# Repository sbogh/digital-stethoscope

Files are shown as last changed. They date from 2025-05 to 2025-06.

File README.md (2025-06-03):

# ScopeFace: Digital Stethoscope

## Table of Contents
- [Introduction](#introduction)
- [Features](#features)
- [Team](#team)
- [Class Assignments](#class-assignments)
- [UX Research](#ux-research)
- [System Design](#system-design)
  - [UI Prototypes](#ui-prototypes)
  - [System Diagrams](#system-diagrams)
  - [Architecture](#architecture)
- [Repo Structure](#repo-structure)
- [Software](#software)
  - [Frontend](#frontend)
  - [Backend](#backend)
  - [Running the App](#running-the-app)
- [Hardware](#hardware)
  - [Setup](#setup)
  - [Operation](#operation)
  - [Assembly](#assembly)
- [Known Limitations](#known-limitations)
- [Future Work](#future-work)

## Introduction
**ScopeFace** is a portable digital stethoscope system developed over 10 weeks as part of UC San Diego's CSE 237D Embedded Systems Project course (Spring 2025). Our goal was to prototype a clinician-focused tool that amplifies, records, and replays heart and lung sounds through a streamlined mobile interface.

Designed with input from nurses, PAs, and doctors, the app supports session-based `.wav` recording, waveform visualization, note-taking, and Firebase-backed data storage. The hardware component captures sound using a custom-built stethoscope device, while the SwiftUI app allows users to review and annotate sessions in real time.

Check out our [external web presence here](https://myrmanshelby.github.io/digital-stethoscope-landing-page/)  
(External web presence [repo linked here](https://github.com/myrmanshelby/digital-stethoscope-landing-page)).

## Features
- Session-based `.wav` recording and playback  
- Waveform visualization  
- Session renaming and note-taking  
- Firebase integration for storage and authentication

## Team
- [Siya Rajpal](https://www.linkedin.com/in/siya-rajpal/): fullstack engineer
- [Shelby Myrman](https://www.linkedin.com/in/shelby-myrman/): ux design/frontend engineer
- [Amrita Moturi](https://www.linkedin.com/in/amrita-moturi/): hardware engineer
- [Shayan Boghani](https://www.linkedin.com/in/shayan-b/): hardware engineer

## Class Assignments
As part of UCSD's CSE 237D course, we created the following project artifacts:
- [Project Proposal](https://github.com/sbogh/digital-stethoscope/blob/main/admin/class-assignments/CSE_237D_Milestone_Report.pdf): A document detailing our project goals, MVP, and timeline
- [Milestone Report](https://github.com/sbogh/digital-stethoscope/blob/main/admin/class-assignments/CSE_237D_Milestone_Report.pdf): A document created halfway through the quarter to update our MVP and timeline
- [Project Update](https://github.com/sbogh/digital-stethoscope/blob/main/admin/class-assignments/ScopeFace%20Project%20Update-2.pdf): Our midquarter presentation updating the class on our progress

## UX Research
Before developing, we conducted user research interviews to gauge user needs. We then looked at app design inspiration and mapped in-app customer journeys. See our UX artifacts below:
- [User Interviews](https://github.com/sbogh/digital-stethoscope/blob/main/admin/user-research/user-research-summary.md)
- [Design Inpsiration](https://github.com/sbogh/digital-stethoscope/blob/main/admin/initial-diagrams/design-inspiration.pdf)
- [Initial User Journey Map](https://github.com/sbogh/digital-stethoscope/blob/main/admin/initial-diagrams/initial-user-journey.pdf)

## System Design

### UI Prototypes
We completed high-fidelity prototypes for both our MVP and ideal full system. 

#### MVP Prototypes
- [Login Flow](https://www.figma.com/design/D0sZ9Dy5eKCmVsZL9oDZRN/Digital-Stethoscope?node-id=1-34&t=OJdkmq2NDCs8I1Uz-1)
- [New Recording Page](https://www.figma.com/design/D0sZ9Dy5eKCmVsZL9oDZRN/Digital-Stethoscope?node-id=60-2107&t=OJdkmq2NDCs8I1Uz-1)

#### Reach System Prototypes
- [Learn More Flow](https://www.figma.com/design/D0sZ9Dy5eKCmVsZL9oDZRN/Digital-Stethoscope?node-id=38-15&t=OJdkmq2NDCs8I1Uz-1)
- [Home Page](https://www.figma.com/design/D0sZ9Dy5eKCmVsZL9oDZRN/Digital-Stethoscope?node-id=47-155&t=OJdkmq2NDCs8I1Uz-1)
- [FAQs Page](https://www.figma.com/design/D0sZ9Dy5eKCmVsZL9oDZRN/Digital-Stethoscope?node-id=60-2147&t=OJdkmq2NDCs8I1Uz-1)
- [History Flow](https://www.figma.com/design/D0sZ9Dy5eKCmVsZL9oDZRN/Digital-Stethoscope?node-id=60-2146&t=OJdkmq2NDCs8I1Uz-1)
- [Patient Flow](https://www.figma.com/design/D0sZ9Dy5eKCmVsZL9oDZRN/Digital-Stethoscope?node-id=78-3089&t=OJdkmq2NDCs8I1Uz-1)
- [Account Page](https://www.figma.com/design/D0sZ9Dy5eKCmVsZL9oDZRN/Digital-Stethoscope?node-id=52-3486&t=OJdkmq2NDCs8I1Uz-1)

### System Diagrams
We created 2 sets of system diagrams: our MVP system and our ideal full product system.
- **MVP System**: See our [MVP System Diagram here](https://github.com/sbogh/digital-stethoscope/blob/main/admin/mvp-product-diagrams/mvp-system-diagram.pdf) and our [MVP Database Schema Diagram here](https://github.com/sbogh/digital-stethoscope/blob/main/admin/mvp-product-diagrams/mvp-database-schema.pdf)
- **Full System**: See our [Full System Diagram here](https://github.com/sbogh/digital-stethoscope/blob/main/admin/full-product-diagrams/reach-system-diagram.pdf) and our [Full Database Schema Diagram here](https://github.com/sbogh/digital-stethoscope/blob/main/admin/full-product-diagrams/reach-database-schema.pdf)

For clearer views of our system diagrams, visit our [Miro board here](https://miro.com/app/board/uXjVI8VBn7o=/?share_link_id=259432345089).

### Architecture
- **Frontend**: SwiftUI-based iOS app tailored for clinician workflow (see [frontend ADR here](https://github.com/sbogh/digital-stethoscope/blob/main/admin/ADRs/042125-Swift.md))
- **Backend**: Python FastAPI service to support future device integrations and analytics (see [backend ADR here](https://github.com/sbogh/digital-stethoscope/blob/main/admin/ADRs/042125-Python-FastAPI.md))
- **Database**: Firebase Firestore and Authentication for secure session tracking (see [database ADR here](https://github.com/sbogh/digital-stethoscope/blob/main/admin/ADRs/042125-Firebase.md)) 
- **Hardware**: Custom stethoscope device with onboard mic and embedded microcontroller (see [all HW ADRs](https://github.com/sbogh/digital-stethoscope/tree/main/admin/ADRs))

## Repo Structure

```text
digital-stethoscope/
│
├── .github/                        # GitHub configuration files
│   └── workflows/                  # CI/CD pipeline setup (e.g., test and deploy scripts)
│
├── admin/                          # Documentation, planning assets, and research
│   ├── ADRs/                       # Architectural Decision Records
│   ├── class-assignments/         # Assignments submitted as part of CSE 237D
│   ├── full-product-diagrams/     # Diagrams for long-term vision of the system
│   ├── initial-diagrams/          # Early conceptual or low-fidelity diagrams
│   ├── mvp-product-diagrams/      # Diagrams focused on MVP system architecture
│   └── user-research/             # Notes and transcripts from stakeholder interviews
│
├── backend/                        # FastAPI backend services (e.g., API endpoints, auth)
│   ├── main.py                     # Entry point for the FastAPI app
│   └── ...                         # Additional modules, routes, and utilities
│
├── hardware/                       # Embedded systems and electronics
│   ├── modules/                    # Modular firmware for sensors, audio processing, etc.
│   ├── design/                     # Hardware design related information
│   │   ├── printing-files/         # CAD design files
│   └── ...                         # Circuit diagram, BOM, README for assembly instructions
│
├── digital-stethoscope/           # SwiftUI iOS app (Xcode project root)
│   └── digital-stethoscopeUITests # SwiftUI testing
│   ├── digital-stethoscope/       # Main app source folder
│   │   ├── Config/                # Environment settings, constants, Firebase setup
│   │   ├── Controllers/           # ViewModels and state management logic
│   │   ├── Extensions/            # Swift extensions for common utilities
│   │   ├── Models/                # Data structures for recordings, sessions, user state
│   │   └── Views/                 # SwiftUI interface components
│   │       ├── LearnMoreFlow/     # "Learn More" educational flow
│   │       ├── LoginFlow/         # Sign-in and account setup screens
│   │       └── RecordingsPage/    # Session list, audio playback, and note-taking
│   └── ...                        # Additional files for assets, userdata etc.
│
└── README.md                       # Project overview and documentation
```

## Software

### Frontend
1. Make sure you have Xcode downloaded on your computer.
2. The app is nested in folders of the same name. When you clone the respository, be sure to open digital-stethoscope/digital-stethoscope
3. Firebase SDK: You must install the Firebase SDK on your own machine.
    1. Navigate to the Project icon and right click (the first digital-stethoscope)
    2. Click on "Add Package Dependencies"
    3. In the search bar that pops up, paste this link: https://github.com/firebase/firebase-ios-sdk
    4. Click "Add Package"
    5. Then look through the list, adding Firebase Auth, Firebase Core, and Firebase FireStore to the target, which is just digital-stethoscope
4. Info.plist: Click on the projet icon one more time
    1. Navigate to the target (the icon labeled digital-stethoscope)
    2. Go to build settings, at the top, and click "all"
    3. Then search for "Generate Info.plist File". It should be under "Packaging". Make sure it is turned to No.
    4. Below that, there will be a field Info.plist File. Ensure the path to the Info file in the cell. 
5. Then you should be good to go!

### Backend
1. Make sure you have Python 3.10+ installed.
2. Make sure to have FastAPI installed
3. Take a look at main.py to get an idea of how everything works.
4. use ```uvicorn main:app --reload``` to run the server

### Testing

We used separate testing frameworks for the backend and frontend to ensure reliability across the system.

#### Backend (FastAPI + pytest)

All backend logic is tested using `pytest`.

To run backend tests:
    ```bash
    cd backend
    pytest

Make sure your virtual environment is activated and all dependencies from requirements.txt are installed.

**Test coverage includes:**
- Endpoint behavior
- Data validation
- Utility functions

#### Frontend (SwiftUI + XCTest)
Frontend tests were written using XCTest in Xcode.

To run frontend tests:
1. Open the Xcode project at digital-stethoscope/digital-stethoscope
2. In the Xcode menu, go to Product > Test

**Test coverage includes:**
- UI behavior of major views
- State updates and view model logic

All tests are located in the Tests group within the Xcode project navigator.

### Running the App
To run ScopeFace locally, start by launching the backend server and then run the iOS app through Xcode.
1. Install dependencies from the `requirements.txt` file:
   ```bash
   cd backend
   pip install -r requirements.txt 
2. Run the server
    ```bash
    uvicorn main:app --reload
3. Open the XCode project at digital-stethoscope/digital-stethoscope
4. Connect your iOS simulator or device and click run in Xcode.

## Hardware

### Setup
1. Using the Arduino IDE, plug in your XIAO ESP32-S3
2. Go to Tools -> PSRAM and enable "OPI PSRAM"
3. Add WiFi SSID and Password Information where specified in instruction comments
4. Add Firebase API Key and double check bucket and user authentication information
5. Compile and upload to microcontroller

### Operation
1. Wait for upload to complete and check for initialization success (serial monitor will display WiFi connected, Firebase connected)
2. Press button to record 30 seconds of audio (LED will be red)
3. Wait for Firebase upload to complete (LED will be green)
4. Navigate to Firebase to playback audio

### Assembly
Please see the BOM [here](https://github.com/sbogh/digital-stethoscope/blob/main/hardware/design/ScopeFace%20BOM.xlsx) for information on the parts you need. See the README [here](https://github.com/sbogh/digital-stethoscope/tree/main/hardware/design#readme) for instructions on creating and assembling the device.

## Known Limitations

- Currently runs only on the iOS simulator (no physical deployment)
- No patient or date search functionality
- No HIPAA compliance implemented
- ML diagnostics and patient profiles are not yet developed

## Future Work

While our MVP successfully supports audio recording and playback through a mobile interface, we do not plan to continue developing this product beyond the scope of our course. However, if we were to bring the app to market, the following areas represent logical extensions based on our prototypes and system design:

### HIPAA Compliance
To prepare the system for real-world clinical use, we would need to implement full HIPAA compliance. This would include encrypted data storage, authenticated access, and audit logging to ensure secure handling of sensitive health information.

### Patient Assignment and Record Management
A full version of the app could support assigning heartbeat and lung recordings to individual patients. This might include:
- Patient profiles
- Recording tagging and linking

See our [Patient Flow Prototype](https://www.figma.com/design/D0sZ9Dy5eKCmVsZL9oDZRN/Digital-Stethoscope?node-id=78-3089&t=OJdkmq2NDCs8I1Uz-1) and [Full System Diagram](https://github.com/sbogh/digital-stethoscope/blob/main/admin/full-product-diagrams/reach-system-diagram.pdf) for intended design.

### History and Session Review
We envisioned adding a history view to allow clinicians to filter by date, patient, or condition to access recordings.

See our [History Flow Prototype](https://www.figma.com/design/D0sZ9Dy5eKCmVsZL9oDZRN/Digital-Stethoscope?node-id=60-2146&t=OJdkmq2NDCs8I1Uz-1).

### Improved Home and Recordings Pages
In a production-ready version, the home and recordings pages could be enhanced to include streamlined navigation across patients and sessions

See our [Home Page Prototype](https://www.figma.com/design/D0sZ9Dy5eKCmVsZL9oDZRN/Digital-Stethoscope?node-id=47-155&t=OJdkmq2NDCs8I1Uz-1) compared to our [MVP Recordings Page](https://www.figma.com/design/D0sZ9Dy5eKCmVsZL9oDZRN/Digital-Stethoscope?node-id=60-2107&t=OJdkmq2NDCs8I1Uz-1).

### Machine Learning for Diagnostics
If continued, we could explore machine learning models for analyzing heart and lung sounds. Features might include:
- On-device or server-side analysis
- Detection of irregular rhythms, murmurs, or wheezing
- Clinician-facing summaries of algorithmic findings

This concept would be positioned as decision support rather than automated diagnosis.

### Deployment and TestFlight
Currently, the app can only be run on a simulator due to the cost of an Apple Developer account. In a future rollout, we would:
- Register for an Apple Developer account
- Use TestFlight to distribute builds to physical devices
- Consider submitting to the App Store for clinical pilots

---

These potential extensions align with the user needs captured in our [User Interviews](https://github.com/sbogh/digital-stethoscope/blob/main/admin/user-research/user-research-summary.md) and the architecture outlined in our [Miro board](https://miro.com/app/board/uXjVI8VBn7o=/?share_link_id=259432345089).

## Contributing
This project is no longer actively maintained, but if you'd like to fork or reuse components, feel free to open issues or pull requests.

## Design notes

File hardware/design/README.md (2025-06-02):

# Assembly Instructions
This document will provide a guide to assembling the ScopeFace Digital Stethoscope. To begin, please review the BOM and ensure you have all of these parts. You will also need 22 AWG Wire, a Soldering Iron, Electrical Tape, PET-G, and a 3D Printer.

First, we will do some preparation work:
1. Solder pieces of 22 AWG wire (longer than you think you'll need) to the following pins of the microphone evaluation board: WS, SCK, Data, GND, VDD. Try to use different colors for easy distinguishing.
2. Solder the Male to Female Battery connector to the XIAO ESP32-S3. Ensure to solder the correct leads. See [here](https://wiki.seeedstudio.com/xiao_esp32s3_getting_started/#battery-usage) for specific instructions.
3. Desolder the button wires and solder them so they go upwards rather than straight outwards. This will help with space management.
4. Solder resistors to the LED leads (only Red and Green). Clip off the Blue lead.

Now we can put together the parts:
1. Print all of the parts found in /printing-files on your 3D Printer in PET-G
2. Take the heated threaded inserts and place them inside the holes on the Diaphragm and Mic Mount. They should slide in all the way except the top section which is not tapered. Using a soldering iron, set these inserts into the part so they are flush with the top surface of the standoffs.
3. Slide the battery into the Battery Mount. Ensure that the wire lead faces the inside of the body and slide it through the small opening to have the wires stick out as the battery sits inside the part.
4. Slide the mic evaluation board into the slot on the Diaphragm and Mic Mount. It should press fit (it is VERY tight so be absolutely sure the pick up hole on the mic board lines up with the hole on the part before pressing it down).
5. Stack the ESP32 Mount and the Battery Mount on top of the Diaphragm and Mic Mount. Using the M2-0.4 x 12 mm bolts secure these parts together using diagonal holes (2 of the four slots). IMPORTANT: route the wires from the battery on the inside of the standoffs so that it sits tightly between the Battery Mount and the standoffs.
6. Place the XIAO ESP32-S3 into the ESP32 Mount. It should slide in and be held in place. Solder the mic evaluation board WS, SCK, and Data cables (see the wiring diagram for specific pins).
7. Take Casing Cover and slide the push button into its slot.
8. Solder the 3.3V power to the microphone board cable (VDD) and the push button NEGATIVE lead.
9. Solder the push button POSITIVE lead to its GPIO pin (see [wiring diagram](https://github.com/sbogh/digital-stethoscope/blob/main/hardware/design/Wiring%20Diagram.png)).
10. Slide the LED into its slot. Solder the red and green pins to their respective GPIO ports (see [wiring diagram](https://github.com/sbogh/digital-stethoscope/blob/main/hardware/design/Wiring%20Diagram.png)).
11. Solder GND to the microphone board (GND) and the LED common ground pin.
12. Attach the antenna to the XIAO ESP32-S3. ([link](https://wiki.seeedstudio.com/xiao_esp32s3_getting_started/#installation-of-antenna))
13. Line up the USB-C opening on the Casing Cover to the XIAO ESP32-S3 port (the button should be opposite to this face) and slide the cover on. It will be tight so be careful to ensure no pinched wires.
14. Use the M2-0.4 X 25 mm bolts to secure the Casing Cover to the heated threaded inserts.
15. Slide the stethoscope diaphragm cover onto the Diaphragm and Mic Mount. It will stretch onto the bottom lip.

Now you can enjoy your ScopeFace Stethoscope!

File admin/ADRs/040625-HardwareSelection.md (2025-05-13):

# Architecture Decision Record: Hardware selection

**Status**: Accepted  
**Date**: 2025-04-06  

---

## 1. Context

Our first stage for hardware selection was determining a good fit for the main component of our embedded system. There are options like the Raspberry Pi (single-board computer), Arduino boards (microcontroller), ESP32 (microcontroller), and others. The selected hardware needs to be capable of connecting components to record and process heart and lung sounds, transmit data wirelessly, and potentially run classification models.

## 2. Decision

Our project requirements lean towards the use of a microcontroller.

## 3. Rationale

A SBC is more complex than is needed for this project given the straightforward use case. Additionally, size constraints make it so that a microcontroller may be a better choice for the product form factor. Potential stretch goals, like onboard ML inference, can still be explored using higher-end microcontrollers like the ESP32-S3.

## 4. Consequences

### Positive outcomes

- Lower cost and power requirements
- Smaller physical footprint
- Easier integration with embedded peripherals like microphones
- Faster development for real-time, single-purpose firmware

### Negative outcomes
- Limited processing power may constrain future ML capabilities or advanced signal
processing

## 5. Alternatives Considered

- Raspberry Pi (e.g., Pico W): Rejected due to lack of Bluetooth on Pico W, higher cost and power usage on full-size Pi models, and overkill for the use case.

- STM32 family: Not chosen due to longer learning curve and less community documentation compared to ESP32.

- ESP32-WROOM-32 / ESP32-S3: These were selected as microcontroller options based on processing capability, wireless features, and documentation maturity.

## 6. References

Raspberry Pi Pico documentation [https://www.raspberrypi.com/documentation/microcontrollers/pico-series.html]

STM32 32-bit Arm Cortex MCUs
[https://www.st.com/en/microcontrollers-microprocessors/stm32-32-bit-arm-cortex-mcus/documentation.html]

ESP32-S3 datasheet and Espressif documentation [https://www.espressif.com/sites/default/files/documentation/esp32-s3_datasheet_en.pdf]

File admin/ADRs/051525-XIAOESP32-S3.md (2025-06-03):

# Architecture Decision Record: [Transition to Seeed Studio XIAO ESP32S3 Plus]

**Status**: [Accepted]  
**Date**: [2025-05-15]  

---

## 1. Context

 Our initial prototype used the standard ESP32-S3 development board. However, the size of the ESP32-S3 dev board created a major constraint for integrating the device into a small shell suitable for clinical or at-home use.

We also wanted to avoid the complexity and cost of designing a custom PCB, as our timeline prioritized rapid prototyping and iteration.
## 2. Decision

We have decided to transition from the standard ESP32-S3 development board to the Seeed Studio XIAO ESP32S3 Plus.

## 3. Rationale

The Seeed Studio XIAO ESP32S3 Plus was selected for the following reasons:

Smaller footprint: The XIAO board’s compact size (21 × 17.5 mm) allows it to be directly integrated into our 3D-printed stethoscope housing without requiring a custom PCB.

Built-in features: The Plus variant includes integrated USB-C, battery charging, and flash/RAM (8MB PSRAM, 16MB flash), which are needed for onboard audio buffering and wireless transmission tasks.

Maintains ESP32-S3 architecture: This transition retains compatibility with our existing codebase, libraries, and development tools.

## 4. Consequences

### Positive outcomes:

Enables a complete prototype build within a standard stethoscope form factor.

Avoids custom PCB design during initial development.

Reduces cost and lead time for prototyping iterations.

Maintains ESP32 toolchain and firmware compatibility.

### Negative outcomes:

May require RF tuning or external antenna in final design if extended WiFi range is needed.

Tighter GPIO constraints and mechanical routing limitations may limit future peripheral expansions.

### Process Changes:

Firmware adapted to match the XIAO ESP32S3 Plus pinout.

CAD models for enclosure updated for new board dimensions and connectors.

Charging and power management tested using integrated USB-C and minimal LiPo battery setup.

## 5. Alternatives Considered

LilyGo T7 S3: Technical specs were sufficient, but was ruled out due to sourcing issues—high price, limited availability, and long shipping times.

## 6. References

Seeed Studio XIAO ESP32S3 Plus (16 MB Flash, 8 MB PSRAM):
https://www.seeedstudio.com/Seeed-Studio-XIAO-ESP32S3-Plus-p-6361.html

LilyGo T7 S3:
https://lilygo.cc/products/t7-s3

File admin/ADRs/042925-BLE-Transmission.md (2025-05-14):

# Architecture Decision Record: Bluetooth Audio Transmission

**Status**: Accepted  
**Date**: 2025-04-25  

---

## 1. Context

The team explored how to transmit audio data from the ESP32 microcontroller to an iPhone via Bluetooth and considered possible architecture designs to handle audio file storage and avoid data loss during transmission.
## 2. Decision

We investigated Bluetooth audio transmission using the ESP32 A2DP profile and a timer-based audio recording trigger (e.g., press button → record for X seconds). We also decided to integrate a microSD card interface for local storage of audio prior to transmission.
## 3. Rationale

The ESP32 supports A2DP (Advanced Audio Distribution Profile) for Bluetooth audio streaming, which seems to be standard. iOS places limitations on BLE connections (such as MTU, packet limitations, transmission intervals). 
For the timer-based recording, this simplifies our firmware logic so that we can press record, record for a fixed time, and auto stop. Local storage via microSD ensures recordings are not lost due to unstable wireless conditions.

## 4. Consequences

### Positive outcomes

- Reduced risk of data loss with local microSD buffering

### Negative outcomes
- Potential delays in file upload if relying on local storage

- Need to manage microSD read/write cycles and file system handling

- Increased firmware and hardware complexity for SD card integration and buffer management

### Changes to processes/systems
- Introduce SD card write/delete logic into embedded software

- Need to evaluate packet framing strategies for .wav file reconstruction (header + raw data)

## 5. Alternatives Considered

Potential pivots based on iOS BLE connection limitations:  Have ESP32 connect either directly to a cloud server gateway or use the app as an authentication gateway to make connection with cloud server and have data transmitted directly there rather than to the iPhone.

## 6. References
Guide for MicroSD Card Module using Arduino IDE
[https://randomnerdtutorials.com/esp32-microsd-card-arduino/]

Challenges in Bluetooth Low Energy (BLE) Integration with iOS Devices
[https://www.zco.com/blog/challenges-in-ble-integration-with-ios-devices/]

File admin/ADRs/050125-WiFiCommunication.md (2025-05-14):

# Architecture Decision Record: Pivot to WiFi Communication and microSD-Based File Storage with Firebase Integration

**Status**: Superseded
**Date**: 2025-05-01

---

## 1. Context

The team initially explored how to transmit audio data from the ESP32 microcontroller to an iPhone via Bluetooth. However, BLE limitations including connection instability, low MTU size, and complexity in handling large file transfers led to reevaluation.

## 2. Decision
Pivot from BLE to WiFi for uploading audio data from the ESP32. We also decided to use Firebase as the backend for file uploads and database management.

## 3. Rationale
- WiFi offers higher bandwidth and greater reliability than BLE for transmitting large audio files. It also avoids limitations of iOS BLE stack, including lack of native BLE file transfer interfaces.

- TA recommendation confirmed WiFi would be more practical within the project’s scope and timeline.
- Firebase is easy-to-integrate with ESP32 and the front-end team was familiar with the framework.

## 4. Consequences

### Positive outcomes
WiFi transmission
- More reliable data transmission via WiFi
  
-  Easier integration with mobile frontend through Firebase

Firebase:
- Provides secure file hosting and database access

- Frontend can easily pull data directly from Firebase without complex middleware

### Negative outcomes
N/A

## 5. Alternatives Considered

As mentioned, we pivoted away from BLE transmission of audio data.
## 6. Related Decisions
BLE Transmission ADR [https://github.com/sbogh/digital-stethoscope/blob/main/admin/ADRs/050925-BLE-Transmission.md]

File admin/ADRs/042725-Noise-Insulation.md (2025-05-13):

# Architecture Decision Record: Noise Insulation Strategy

**Status**: Accepted 
**Date**: 2025-04-27 

---

## 1. Context

During testing, it became clear that the microphone alone was too sensitive to ambient noise. To address this, the team researched acoustic insulation strategies to shield the microphone from external noise sources.
## 2. Decision

Based on our research, we will prototype a noise insulation solution using a construction-grade ear protection cup as a sound-dampening casing for the microphone. We will route microphone wiring through the ear cup and seal it to prevent sound leakage.

## 3. Rationale

The microphone is highly sensitive and picks up unwanted ambient sounds, which hinders the clarity of heartbeat/lung sounds. A construction ear protector offers a cost-effective and accessible solution for prototyping a noise-insulating material.

## 4. Consequences

### Positive outcomes
- Minimal-cost prototype with quick testability using off-the-shelf materials
### Negative outcomes
- Drilling ear cup and sealing introduces irreversible changes to prototype components

### Any changes to processes, systems, or dependencies
- Microphone wiring must be adapted to route through physical insulation

## 5. Alternatives Considered

Using commercial stethoscope housing: Considered overkill for early prototyping and lacks flexibility.
## 6. Related Decisions

N/A

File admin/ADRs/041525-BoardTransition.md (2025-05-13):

# Architecture Decision Record: Transition to ESP-WROOM-32 with Digital Microphone

**Status**: Accepted  
**Date**: 2025-04-15  

---

## 1. Context

The team conducted testing with both analog and digital microphones on selected MCU boards (ESP32-S3 and ESP-WROOM-32) to identify the best microphone for capturing heart/lung sounds and verify compatibility with the microcontroller platform.

## 2. Decision

Microphone testing occurred and based on outcome the digital microphone was chosen. The initial ESP32 S3 board failed to interface with the microphone so the ESP-WROOM-32 has been made the primary board.

## 3. Rationale

Mic Selection: 
- The analog microphone (MAX4466) suffered from heavy power supply noise and delivered poor sound quality, and failed to filter noise effectively.

- The digital microphone (INMP441) leveraged the I2S interface on ESP32 boards allowing seamless and quick setup.

- The use of a digital mic also eliminates the need for external ADCs, simplifying hardware design.

Board Selection:

- The ESP32-S3 failed to recognize any serial data over I2S from the INMP441 during testing.

- The ESP-WROOM-32 successfully captured audio from the digital microphone and was thus selected as the new primary board for development.

Additional considerations included:

- Aliasing and mssing low frequencies: These issues can be mitigated by selecting an appropriately high sampling rate.

- File size and audio compression: The raw audio data can be stored in WAV format (lossless) or transmitted as raw bytes and reconstructed server-side

- Bluetooth transmission limits: Live streaming of audio via BLE may not be feasible; however, delayed upload is acceptable our use case.

## 4. Consequences

### Positive outcomes

- Improved audio quality and reduced noise using INMP441
- More stable and compatible development environment using ESP-WROOM-32
- Simplified integration path via I2S (no need for ADC)

### Negative outcomes
- Not using the ESP32-S3 forfeits potential for onboard AI inference unless revisited

### Changes to processes/systems
- Transition away from analog signal processing to digital-only audio handling

- Firmware updates to focus exclusively on I2S and ESP-WROOM-32 compatibility

- Audio files will likely be recorded in WAV format

## 5. Alternatives Considered

N/A

## 6. Related Decisions
MCU Decision
[https://github.com/sbogh/digital-stethoscope/blob/main/admin/ADRs/040725-MCU-Decision.md]

Mic Selection
[https://github.com/sbogh/digital-stethoscope/blob/main/admin/ADRs/040825-MicSelection.md]

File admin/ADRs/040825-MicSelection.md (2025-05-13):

# Architecture Decision Record: Microphone selection

**Status**: Accepted  
**Date**: 2025-04-08 

---

## 1. Context

The team decided to test both analog and digital microphones with the devices to determine the best device to use to capture heart and lung sounds. The microphones with the correct frequency ranges are difficult to source so initial testing will be done with common microphones easily available and then when a decision is made (between digital and analog), the microphone will be swapped for the true device.

## 2. Decision

Our team decided to test both an analog microphone (MAX4466) and a digital microphone (INMP441).

## 3. Rationale

Frequency range: Both MAX4466 and INMP441 can support frequencies near the required 20–3000 Hz range.

Sampling rate: Both mics support a sampling rate 2x of highest frequency

Availability and cost: Both microphones are inexpensive and widely available, which is ideal for our initial prototype.

## 4. Consequences

### Positive outcomes

- INMP441 (digital): Uses I2S protocol, avoiding analog signal interference. I2S is natively supported on ESP32 and has reliable open-source examples and community support.

### Negative outcomes
- MAX4466 (analog) requires analog-to-digital conversion (ADC) and may introduce analog noise. Also, the ESP32-S3 does not have built-in ADC, requiring external components.

## 5. Alternatives Considered

N/A

## 6. References

Heart and lung frequencies [https://pmc.ncbi.nlm.nih.gov/articles/PMC2990233/#:~:text=The%20spectrum%20of%20heart%20sounds,like%20fine%20or%20coarse%20crackles.]

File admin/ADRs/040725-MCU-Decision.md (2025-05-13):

# Architecture Decision Record: MCU decision

**Status**: Accepted 
**Date**: 2025-04-07 

---

## 1. Context

The team decided on an MCU after considering other embedded device options due to the need for the system to be low-cost and being able to handle wireless connectivity and potentially ML inferencing.

## 2. Decision

Based on the stretch goal the ESP32 S3 was chosen, with the ESP-WROOM-32 chosen as a secondary fallback.

## 3. Rationale

Key considerations included budget constraints, time constraints (well documented board), and connectivity functionality (need for BLE/WiFi).
ESP32 S3 contains a strong processing unit capable of onboard inference for an AI model (a potential stretch goal for the team)

## 4. Consequences

### Positive outcomes
- The ESP32-S3 Dev Module has strong processing capabilities, allowing future support for onboard AI inference
- Leverages well-supported and cost-effective components
### Negative outcomes
- ESP32 S3 does not contain built-in ADC so audio out would likely require additional components
- ESP32-S3 is newer, so some libraries or integrations may be less mature than ESP-WROOM-32.

### Any changes to processes, systems, or dependencies
- Since ESP32 S3 does not contain an ADC, we may have to consider other mic interfaces like I2S

## 5. Alternatives Considered

Arduino Nano ESP32 user experience research shows that the interface is not aligned with traditional ESP32 use and will require additional research to understand some niche aspects of connecting peripheral devices
ESP-WROOM-32 is the best documented of all devices, but may not be able to handle the ML inferencing computational requirement.

## 6. Related Decisions

N/A

## 7. References

Esp32-wroom-32 docs [https://www.espressif.com/sites/default/files/documentation/esp32-wroom-32_datasheet_en.pdf]

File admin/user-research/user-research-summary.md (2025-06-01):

# User Research Summary

## April 2, 2025: Shelby's Discussion with Nurses

### Requested Use Cases from a Small Sample of Nurses and Physician Assistants

#### Cost
- Stethoscopes are expensive, often costing at least $100 out of pocket.
- Nurses prioritize performance and are willing to pay for quality.
- **Our solution**: Create a significantly more affordable alternative.

#### Difficulty Hearing
- Nurses report that stethoscope sounds are often too quiet.
- One nurse was unable to hear wheezing that her trainer could, even after repeated attempts.
- **Our solution**: Integrate sound amplification.

#### Confirming Sounds with Doctors
- A nurse identified a murmur that was not heard by a physician during follow-up, leading to uncertainty.
- Having a recording to replay for confirmation would be helpful.
- **Our solution**: Enable sound recording and playback.

#### Difficulty Counting
- Nurses struggle with counting beats per minute (BPM) and respirations while listening for anomalies.
- **Our solution**: Provide automatic BPM and respiration rate counting.

#### Portability and Usability
- Nurses often misplace stethoscopes.
- Pediatric nurses report that traditional stethoscopes can scare children.
- **Our solution**: Consider a compact, wearable, or pin-based form factor with a friendly design.

#### Live Listening
- Some assessments are time-sensitive and require immediate feedback.
- **Our solution**: Support live listening via speakers or Bluetooth-connected headphones.

---

## Other Considerations

### Pediatric Use
- Traditional stethoscopes have a baby-specific diaphragm.
- Using the adult side on a baby results in excessive noise and poor sound isolation.
- **Note**: Our design may need a smaller sensor or a separate pediatric version.

### Machine Learning Diagnostics
- Nurses support ML-aided diagnostics, but prioritize reliable amplification and recording.
- Users want access to recordings even if automated diagnosis is included.
- **Our solution**: Focus on recording, with ML as an optional aid.

### Lungs
- Stethoscopes are also used for lung auscultation.
- Lung and heart sounds are distinct; users may need to indicate which organ is being monitored.
- **Our solution**: Offer a simple toggle between heart and lung modes.

---

## April 4, 2025: Shayan’s Discussion with a Doctor

### Clinical Use Cases During Exams

#### Heart Rate
- Categories: bradycardia, normal (60–100 bpm), tachycardia

#### Rhythm
- Regular or irregular
  - Irregularly irregular (e.g. atrial fibrillation)
  - Episodic irregular
  - Premature beat

#### Heart Sounds
- S1: Closure of mitral and tricuspid valves
- S2: Closure of aortic and pulmonary valves

##### Important Sound Features
- Sound intensity: muffled, too loud, normal
- Split sounds: generally not prominent in adults
  - S1: mitral before tricuspid
  - S2: aortic before pulmonary
- Murmurs: may indicate normal or pathological flow
  - Example: anemia can cause high flow murmurs

##### Murmur Classification
- Phase: systolic (S1–S2) or diastolic
- Timing: early, late, throughout
- Special case: machinery murmur (present in both phases)

#### Note
- Many doctors now rely on ECGs instead of stethoscopes.

---

## April 4, 2025: Amrita’s Meeting with Nicolay (Sensor Specialist)

### Technical Feedback and Suggestions

- The stethoscope’s listening component is complex enough to justify a full project focus.
- Consider creating a disposable patch version with external electronics.
- Companies in this space include Eko and Korean pet care companies using Bluetooth-enabled stethoscopes.

### Hardware Considerations

- Evaluate whether the **NDP120** chip can handle onboard inferencing.
- Explore **PDM** output format for sensor-to-dev board interfacing.
- Use an **audio codec chip** to translate raw sensor data into a usable format.

### Sensor Recommendations

- Consider analog sensors for better compatibility with audio processing.
- Prioritize small form factor and low noise for clean signal capture.
- V2S sensor operates at 10 kHz, but heart sounds are below 500 Hz.
  - Excessive bandwidth introduces noise; filtering is necessary.
  - Prefer sensors with native bandwidth under 1 kHz.

### Additional Notes

- Explore accelerometers and vibration sensors as alternatives.
- Arduino Nano 33 supports PDM input and could be a good prototyping option.

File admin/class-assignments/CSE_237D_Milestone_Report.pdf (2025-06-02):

# CSE 237D: Digital Stethoscope Milestone Report

### Amrita Moturi, Shayan Boghani, Shelby Myrman, Siya Rajpal

UC San Diego Computer Science & Engineering Dept.

## MVP Progress

### Proposed MVP

In our Project Specification Report, we laid out our initial vision for our original MVP below.
The goal of our Minimum Viable Product (MVP) is to develop a fully functional and portable digital stethoscope that captures, amplifies, records, and visualizes heart and lung sounds. This MVP serves as a proof-of-concept, providing the foundational system architecture for our broader vision while allowing us to gather early user feedback and iterate over time. Our emphasis is on incremental improvement: each core function is selected for high feasibility and clear alignment with the project’s long-term clinical goals which can be decoupled and tested as we make progress.

Core MVP Components

1. Acoustic Signal Acquisition: The MVP will use a digital microphone with sensitivity in the appropriate frequency bands for heart and lung sounds. The system will be integrated into a robust enclosure modeled after existing stethoscope chest pieces to facilitate familiarity and ergonomics.
2. Recording and Playback: The MVP must reliably capture sound data for local storage and enable playback through either a speaker or through the front end software interface. Data will be stored securely

1

and labeled with timestamps, creating a foundation for potential clinical documentation or further diagnostic analysis.

3. Portable and Durable Hardware Design: The stethoscope will be encased in a 3D-printed shell that is both lightweight and resilient. It will house the microcontroller, power supply (battery), and microphone. The prototype will prioritize modularity to support future iterations, such as integration of custom PCBs or embedded ML components.
4. Visualization via Companion Interface: The MVP will include a simple user interface (UI) that visualizes the sound waveform and increases the sound captured by the device. This UI will be implemented either as a mobile app based on preliminary user research and will focus on clarity and usability. The visualization and audio allows real-time signal monitoring, enabling both users and potential clinical testers to assess stethoscope performance.

The MVP is intentionally narrow in scope but complete in functionality. Each feature is selected to highlight a critical part of the user experience and overall system integrity. The emphasis is not on completeness or polish but on creating an end-to-end experience that can be tested, validated, and iterated upon. By grounding the MVP in core biomedical functionality (amplification, recording, and visualization), we create a minimum usable product that is meaningful to stakeholders and can evolve based on feedback.
The MVP enables us to evaluate core assumptions about hardware compatibility, UI requirements, and clinical relevance before committing to more complex features such as headphone integration, HIPAA compliance, edge ML deployment, or custom PCB creation. It also provides an anchor for testing usability, sound quality, and data handling practices early in the development lifecycle. Ultimately, our MVP will demonstrate that a portable, secure, and intelligible digital stethoscope can serve as a launchpad for more advanced diagnostic tools and integration with health information systems.

### MVP Progress Evaluation

The above four key components of our MVP can be individually evaluated to determine the team’s progress.

2

1. Acoustic Signal Acquisition: The current device now uses a digital I2S microphone that has the proper frequency band to acquire heart and lung sounds. This microphone took some time to source, and as such testing was done with a more commonly available microphone. However, the microphone was swapped out and has been tested in the audio pipeline that was built out previously.
2. Recording and Playback: The audio pipeline has been rigorously tested to ensure robust quality throughout. The device is able to record and transmit information consistently and effectively for playback from our secure database. Each recording has metadata including: Device ID, Recording ID Number, and Reception Timestamp. These three identifiers allow for easy identification of each new recording.
3. Portable and Durable Hardware Design: This aspect of the device is currently a work in progress. The remainder of the quarter will be dedicated to creating this housing and testing it. This task will entail: designing the casing which allows the microphone to pick up key frequencies, ensuring this casing is robust (drop and water resistance), and finally integrating feedback into the casing design based on further user research.
4. Visualization via Companion Interface: This aspect of the product is currently a work in progress. We have developed the login, authentication, and most of the front-end of the new recording page. During week 7-8, we will pull device data from Firebase for the new recordings page and visualize the waveforms in the app. Additionally, while the data will be retrieved quickly, we will not monitor the signal in real-time, and there may be a lag due to our logistic and privacy-based decision to not upload from the device directly to a user’s phone. We have accounted for this in our UX design to ensure the user experience still feels seamless.

### Milestone and Deliverable Progress

Below, we lay out the milestones and deliverables proposed in our initial report and display the progress made as of this report.

3

Hardware

- Deliverable 1 (Week 3): Hardware Schematic Diagram (Amrita)
Proof: Document with all major hardware components mapped out Milestones:

– Determine and list major components needed based on final product requirements

– Determine connections and additional interfacing components

Progress: Here (https://docs.google.com/spreadsheets/d/1qTJ2odaX2M_xSuLlmmqz6MXSB-b1hMWjHKfpnbmQvbA/edit?usp=sharing) is the BOM regarding the critical components related to the hardware. This has been updated since Week 3 to reflect iterations in the hardware. Here (https://docs.google.com/drawings/d/1nCev1_cij9lSaxVhKZNDl6bqoeuCaXK7Ml2xmFv6oDM/edit?usp=sharing) is the Hardware Schematic Diagram which shows how the different components must be mapped/connected.

- Deliverable 2 (Week 3): Hardware Selection Decision (Shayan) Proof: Bill of materials based on hardware schematic diagram Milestones:

– Research and downselect microcontrollers

– Test microphones for heart and lung sound frequencies

– Decide on filtering approach (analog and/or digital) to isolate target frequency bands for heart (typically 20–150 Hz) and lung (100–1000 Hz) sounds

Progress: As referenced above, the BOM also served as the list of major components needed. Here (https://docs.google.com/spreadsheets/d/1qTJ2odaX2M_xSuLlmmqz6MXSB-b1hMWjHKfpnbmQvbA/edit?usp=sharing) is the BOM which includes the chosen microcontroller and microphone with the proper frequency range. This document (https://docs.google.com/document/d/19m3-ZZDV7gM7EtZsWnEW9_dwk2fAkhaoKPsgd79wpz4/edit?usp=sharing) contains details in how the hardware was chosen.

– Hardware Selection ADR: (https://github.com/sbogh/digital-stethoscope/blob/main/admin/ADRs/040625-HardwareSelection.md) Explains our decision to use a microcontroller for our system

– MCU ADR: (https://github.com/sbogh/digital-stethoscope/blob/main/admin/ADRs/040725-MCU-Decision.md) justifies our use of the ESP32 S3

– Microphone Selection ADR: (https://github.com/sbogh/digital-stethoscope/blob/main/admin/ADRs/040825-MicSelection.md) provides context for use of MAX4466 (analog) and INMP441 (digital) mics

– Board Transition ADR: (https://github.com/sbogh/digital-stethoscope/blob/main/admin/ADRs/041525-BoardTransition.md) describes our initial transition to ESP-WROOM-32 board

4

- Deliverable 3 (Week 5): Initial Product Prototype (Shayan) Proof: Prototype with fully integrated hardware components Milestones:

– Order and assemble hardware

– Wire components, create documentation and diagram

Progress: The initial hardware prototype can be seen in the demo video here. (https://drive.google.com/file/d/16t6yuFCVIlv_w8SWK52N-YrlvbcqlBcp/view?usp=sharing) A newer, more streamlined version can be seen here. (https://drive.google.com/file/d/12NFOvNi5C9KDR8bGgvmpbmkIhpaNUu-6/view?usp=sharing)

- Deliverable 4 (Week 5): Initial Prototype Code (Amrita) Proof: Run and test hardware code, graphs showing frequency response before and after filtering, video demonstration
Milestones:

– Microphone data acquisition and processing

– Recording functionality

– Implement digital filtering to isolate relevant sound frequencies

– Transmit data from microcontroller to device

Progress: The initial prototype code can be seen functioning in the demo video here. (https://drive.google.com/file/d/16t6yuFCVIlv_w8SWK52N-YrlvbcqlBcp/view?usp=sharing) The source code can be found in the GitHub repository here. (https://github.com/sbogh/digital-stethoscope/blob/main/hardware/hardware.ino)

Software

- Deliverable 1 (Week 2): Tech Stack Decision (Shelby) Proof: Tech stack list and rationale
Milestones:

– Compare options and finalize stack

– Write setup guide

Progress: We have finalized our software technology stack, completed the setup guide, and documented our decisions in a series of ADRs.

– Setup Guide: (https://github.com/sbogh/digital-stethoscope/blob/main/README.md) Explains how to run our demo code after downloading the repository.

5

– Firebase ADR: (https://github.com/sbogh/digital-stethoscope/blob/main/admin/ADRs/042125-Firebase.md) justifies our use of Firebase Authentication and Firestore for backend data storage and user management

– SwiftUI ADR: (https://github.com/sbogh/digital-stethoscope/blob/main/admin/ADRs/042125-Swift.md) describes our decision to use Swift and SwiftUI based on user preference for native iOS apps

– Python/FastAPI ADR: (https://github.com/sbogh/digital-stethoscope/blob/main/admin/ADRs/042125-Python-FastAPI.md) outlines why we chose Python with FastAPI for our backend services

- Deliverable 2 (Week 2): GitHub Setup (Siya)
Proof: Screenshot of repo and CI/CD pipeline Milestones:

– Initialize repo

– Add CI/CD for linting and testing

Progress: We have created our repository and organized it. A screenshot of it can be seen Here. (https://drive.google.com/file/d/1JFufRA8rSI2mRyEmdqVacoP95BO5NVBz/view?usp=sharing) We chose to organize the repository by hardware code, backend software code, and our Xcode project, digital stethoscope. We have also included an admin folder in which you can find our system diagrams, and our ADRs.

We have also completed the CI/CD pipeline. Seen in this (https://drive.google.com/file/d/1weWF-WeCU9bcDaMqvMMGQ0uqNd1LX4zg/view?usp=sharing) screenshot of our GitHub actions, there are four workflows. Two for our Python backend, and two for our Swift frontend. You can see that the tests are run for every pull request, or any push or merge to our main branch. This ensures that we maintain good code quality. Note that the Pytest action is failing, because we are yet to write tests for all compoents of our backend. Our workflows can be found in our repository, (https://github.com/sbogh/digital-stethoscope) under .github/workflows.

- Deliverable 3 (Week 4): UI Prototyping (Shelby)
Proof: Wireframes and architecture document Milestones:

– Create Figma wireframes

– Diagram architecture for modularity

Progress: We have completed our high-fidelity wireframes and system architecture for both the MVP and future versions of the system. This (https://miro.com/app/board/uXjVI8VBn7o=/?share_link_id=974447866966)

6

Miro board contains our full Reach system software diagram and MVP system diagram, including database schematics for both.

You can find the MVP wireframes on Figma at the following links:

– Login Flow (https://www.figma.com/design/D0sZ9Dy5eKCmVsZL9oDZRN/Digital-Stethoscope?node-id=1-34&t=OJdkmq2NDCs8I1Uz-1)

– New Recording Page (https://www.figma.com/design/D0sZ9Dy5eKCmVsZL9oDZRN/Digital-Stethoscope?node-id=60-2107&t=OJdkmq2NDCs8I1Uz-1)

We also created wireframes for the complete reach system:

– Learn More Flow (https://www.figma.com/design/D0sZ9Dy5eKCmVsZL9oDZRN/Digital-Stethoscope?node-id=38-15&t=OJdkmq2NDCs8I1Uz-1)

– Home Page (https://www.figma.com/design/D0sZ9Dy5eKCmVsZL9oDZRN/Digital-Stethoscope?node-id=47-155&t=OJdkmq2NDCs8I1Uz-1)

– FAQs Page (https://www.figma.com/design/D0sZ9Dy5eKCmVsZL9oDZRN/Digital-Stethoscope?node-id=60-2147&t=OJdkmq2NDCs8I1Uz-1)

– History Flow (https://www.figma.com/design/D0sZ9Dy5eKCmVsZL9oDZRN/Digital-Stethoscope?node-id=60-2146&t=OJdkmq2NDCs8I1Uz-1)

– Patient Flow (https://www.figma.com/design/D0sZ9Dy5eKCmVsZL9oDZRN/Digital-Stethoscope?node-id=78-3089&t=OJdkmq2NDCs8I1Uz-1)

– Account Page (https://www.figma.com/design/D0sZ9Dy5eKCmVsZL9oDZRN/Digital-Stethoscope?node-id=52-3486&t=OJdkmq2NDCs8I1Uz-1)

- Deliverable 4 (Week 4): Frontend and Backend Setup (Siya) Proof: Video explanation of system
Milestones:

– Backend init, sample route, local DB

– Frontend init and routing

Progress: We have successfully set up both our backend and our frontend. Videos walking through the structure/set up of both are below:

– Backend Setup Walkthrough (https://drive.google.com/file/d/1GVsJC1heAnbWq1pHbTnLi3vXmpb4FhEi/view?usp=share_link)

– Frontend Setup Walkthrough (https://drive.google.com/file/d/1sFWmXqGkKD9TP4UuFYotkBrzWe-anjip/view?usp=share_link)

- Deliverable 5 (Week 5): Deploying Test App (Shelby) Proof: Picture of test app on iPhone
Milestones:

– Configure deployment and fix permission issues

– Upload to Apple test platform and test usability

7

Progress: After further research, we found that deploying a test app via TestFlight requires an Apple Developer Account, which costs $99 per year. While we initially considered using TestFlight to demo our working app, we determined that using the iPhone simulator in Xcode serves our current needs without incurring additional costs. As a result, we decided not to proceed with TestFlight at this stage. For more details, see our No TestFlight ADR here. (https://github.com/sbogh/digital-stethoscope/blob/main/admin/ADRs/050824-NoTestFlight.md)

- Deliverable 6 (Week 5): Add Authentication (Siya)
Proof: Video of working auth flow
Milestones:

– Backend schema and session logic

– Frontend login and API integration

Progress: We have completed the authentication flow end to end. Upon the creation of an account, it verifies that the user does not already have an account and assigns the user a distinct authentication token. From there, when logging in, it verifies the user based on the information stored, and gathers user data from the database. See our authentication flow walk through here. (https://drive.google.com/file/d/1XBg1HMEEGHPknkqUCU6AM9sL0w-Hw25K/view?usp=share_link)

## Future Steps

### Milestones and Deliverables

Hardware

- Deliverable 5 (Week 7): Design and build casing for initial prototype (Shayan)
Proof: Take pictures of the assembled product and test to ensure all functionality still works with casing added
Milestones:

– Design casing in CAD and add hardware components to ensure dimensioning and tolerancing

– 3D print casing

– Assemble product

8

– Test product and ensure all functionality remains

- Deliverable 6 (Week 7): Transmit data from hardware device to database (Amrita)
Proof: Document process and have test data samples that have come from hardware in database
Milestones:

– Set up communication from hardware device to external gateway

– Work with software team to ensure proper routing of received data from gateway to database

– Perform repeatability testing to ensure that data transmission is consistent and the quality of data does not degrade across trials

- Deliverable 7 (Week 9): Refine prototype design (Shayan) Proof: New CAD design for the product which has a focus on ruggedness and ergonomics
Milestones:

– Get feedback from medical professionals on design

– Incorporate feedback to make the product more useable

– Improve casing to be drop resistant and have some water resistance for key components

- Deliverable 8 (Week 9): Create the minimum viable product (Amrita)
Proof: Minimum Viable Product in hand
Milestones:

– Reprint casing and assemble product

– Test product to ensure all functionality maintains previous quality

- Deliverable 9 (Week 10): Create documentation for product (Shayan and Amrita)
Proof: Documents related to product and its abilities and use cases Milestones:

– Compile documentation from full product development

9

– Write product documentation to improve useability and adoption – Write specifications sheet related to limitations and expected use cases including safety information

Software

- Deliverable 7 (Week 8): UI Complete (Shelby) Proof: App walkthrough video
Milestones:

– Build and route core pages
– Write tests and handle edge cases
- Deliverable 8 (Week 8): Integration Test + Tagging (Siya) Proof: Screenshot of database with tags
Milestones:

– Backend fetching and tagging
– Integrate simple waveform display for audio recordings – Connect live frontend-backend and verify E2E
- Deliverable 9 (Week 10): Web Presence (Shelby) Proof: Link to website
Milestones:

– Create and deploy webpage

- Deliverable 10 (Week 10): Additional Testing (Siya) Proof: Screenshot of Testing scripts passing on Github Actions Milestones:

– Additional frontend and backend testing

– End to End testing

### Schedule and Prioritization

Key | Priority
P0 | Critical
P1 | Important
P2 | Stretch

10

Hardware

Milestone/Deliverable | Task | Due Date | Priority
Milestone | CAD Design for Dimensioning | May 16th | P0
Milestone | 3D Print Casing | May 16th | P0
Milestone | Assemble product | May 16th | P0
Milestone | Test product functionality | May 16th | P0
Deliverable | Design and build initial prototype | May 16th | P0
Milestone | Communicate from device | May 16th | P0
Milestone | Data route integration with software | May 16th | P0
Milestone | Repeatability testing | May 16th | P0
Deliverable | Data transmission to database | May 16th | P0
Milestone | User Feedback | May 30th | P1
Milestone | Incorporate feedback | May 30th | P1
Milestone | Rugged Casing Design | May 30th | P1
Deliverable | Refine prototype design | May 30th | P1
Milestone | Assemble refined product | May 30th | P1
Milestone | Test refined product | May 30th | P1
Deliverable | Create the minimum viable product | May 30th | P0
Milestone | Compile dev documentation | June 6th | P0
Milestone | Write product documentation | June 6th | P0
Milestone | Write spec sheet | June 6th | P0
Deliverable | Compile all product documentation | June 6th | P0

Software

11

Milestone/Deliverable | Task | Due Date | Priority
Milestone | Build and route core pages | May 23rd | P0
Milestone | Write tests & handle edge cases | May 23rd | P1
Deliverable | UI Complete | May 23rd | P0
Milestone | Backend fetching and tagging | May 23rd | P0
Milestone | Integrate simple waveform display | May 23rd | P0
Milestone | Connect frontend-backend + verify E2E | May 23rd | P0
Deliverable | Integration Test + Tagging | May 23rd | P0
Milestone | Create and deploy webpage | June 7th | P1
Deliverable | Webpresence | June 7th | P1
Milestone | Additional frontend + backend testing | June 7th | P1
Deliverable | Additional testing | June 7th | P1

Change in Deliverables Reasoning:

Software, Deliverable 10: As mentioned above, deploying our app to Test Flight requires an Apple Developer account, which costs $99. The iOS simulator built into Xcode is sufficient for UI/UX testing and displaying our software end to end. Instead, we will use that time to fine-tune our backend and frontend unit tests along with end-to-end testing to ensure perfect functionality, which addresses the feedback we received to improve our testing infrastructure.

## Project Specification Feedback

The Project Specification had some key feedback which the team incorporated into our progress.
- Building a complete system, from scratch, in 10 weeks is very ambitious. That is your biggest risk.
On the software side, we have specified a reasonably-scoped MVP (a login flow and recording display page) to prioritize device data-capture and proof-of-concept. This way, if we do not complete our stretch features, such as patient linking, we will still have a working product that meets core user needs of amplification and playback.

Hardware progress has been strong and the remaining tasks fit well in our remaining time frame. We did however choose to develop segments of the hardware (microphone acquisition, recording trigger, WiFi

12 connection, Firebase connection, simple Firebase upload) so that each could be demonstrated independently with its own test code. This was very helpful in the integration phase as each process was fully developed. The main task became ensuring the available resources were used properly and without processes disrupting each other.

- Think carefully about how to put the system into parts and allow those parts to be demonstrated individually.
On the software side, we have demonstrated this in our system diagrams. We are developing our software in 4 separate phases, with the first being our MVP. We can also demonstrate components of our MVP individually in various different ways. Our git commit history provides an extremely detailed demonstration of our system. Additionally, our MVP can be split into two parts: the authentication flow and the recording flow, and these can be demonstrated separately.

The hardware was decoupled into task development. Each task that needed to be accomplished had its own test code written. This code was isolated to the basic functionality of that task. Once this code was tested and proven to be robust, it was integrated into the full workflow. The different tasks we identified were as follows:

– Connect to WiFi (link, (https://github.com/sbogh/digital-stethoscope/blob/main/hardware/modules/WiFi_Module.ino) ADR) (https://github.com/sbogh/digital-stethoscope/blob/main/admin/ADRs/050125-WiFiCommunication.md)

– Read button press from GPIO port (link) (https://github.com/sbogh/digital-stethoscope/blob/main/hardware/modules/Button_Module.ino)

– Read and display serial data from microphone on Serial Monitor in Arduino IDE using I2S protocol (link) (https://github.com/sbogh/digital-stethoscope/blob/main/hardware/modules/Mic_Module.ino)

– Use button press to read data from microphone and display results in Serial Monitor (link) (https://github.com/sbogh/digital-stethoscope/blob/main/hardware/modules/Button_Mic_Module.ino)

– Access and store items on microSD card using SPI protocol (link) (https://github.com/sbogh/digital-stethoscope/blob/main/hardware/modules/SD_Module.ino)

– Store sample WAV file on microSD card and check output by playing back audio from microSD card on laptop (link) (https://github.com/sbogh/digital-stethoscope/blob/main/hardware/modules/Store_WAV_Module.ino)

– Connect to Firebase and transmit sample audio recording (prerecorded) to Firebase Storage and compare WAV file on microSD card to file in bucket (link) (https://github.com/sbogh/digital-stethoscope/blob/main/hardware/modules/Firebase_SendAudio_Module.ino)

– Enable PSRAM and use to store audio data in buffer (link, (https://github.com/sbogh/digital-stethoscope/blob/main/hardware/modules/PSRAMBuffer_Module.ino) ADR) (https://github.com/sbogh/digital-stethoscope/blob/main/admin/ADRs/050925-MicroSD-Removal.md)

13

By decoupling these tasks, we sped up development and were able to integrate modules more seamlessly than attempting to write a monolithic codebase.

- Testing infrastructure could use more thought. How will you test the individual components? How will you test the entire system?

We will test individual software components using unit tests written in Python and Swift, depending on the module. Integration tests will ensure interoperability between modules, and end-to-end testing will validate the full pipeline from input to output.

Hardware testing is demonstrable through the module development code. Each component of the system can be isolated and tested. Additionally, the full pipeline can be debugged through the Serial Monitor if needed.

For full system testing, we’ll simulate real-world scenarios and inputs, using both automated and manual tests. Testing is now accounted for in our project milestones, with dedicated time allocated to verify functionality at each phase.

- Documentation process could be better articulated. What exactly will you put into the repo?
We have improved our documentation process, and have defined what will go in the repository. We have organized the repository so the frontend code, the backend code, and the hardware code each have their own directory. Our README contains a setup guide, which we will expand as our project grows. We have also created an admin drectory containing system diagrams and ADRs. This directory will aid in documenting each stage of the development process, and inform the choices we made along the way. Additionally, logs are kept for daily progress on hardware here. (https://docs.google.com/document/d/19m3-ZZDV7gM7EtZsWnEW9_dwk2fAkhaoKPsgd79wpz4/edit?usp=sharing) These coincide with the hardware ADRs written for major decisions.

## Oral Presentation Feedback

A few key updates have been made given this feedback:

14

- Think more broadly about motivation. Maybe it could be used at home for people who don’t want to have a stethoscope. That recording could also be done in remote visits with a doctor?

These comments have given us some ideas on how to shift our user research toward learning more about pain points regarding telehealth. We might also benefit from learning about how incorporating heart and lung sounds into health records might help medical professionals when evaluating patients in this context. People with high blood pressure often own devices at home to help them consistently monitor their readings. Similarly, a potential use case for our device would be to help those with pre-existing conditions monitor their heart and lung health without the need of a doctor visit. Rather than needing a complete stethoscope at home, our system could act as a device to record data and share it remotely with health providers.

- Longer term doing some processing on device to analyze the heart would be valuable. That could be a simple as feedback on whether the signal is good

A stretch goal for the team is to perform onboard processing of the acquired audio data. Initially, our focus was to determine abnormalities that the patient needed to be made aware of immediately. However, it may be helpful to give the patient feedback on how they are operating the device (i.e. in telehealth use cases) to ensure they make adequate contact. This may be added as a long term goal due to time constraints.

15

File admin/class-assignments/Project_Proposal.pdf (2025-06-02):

# CSE 237D: Digital Stethoscope Project Specification

### Amrita Moturi, Shayan Boghani, Shelby Myrman, Siya Rajpal

UC San Diego Computer Science & Engineering Dept.

## Project Charter

### Project Overview

Despite significant technological advancements, most healthcare professionals still rely on traditional stethoscope designs that have remained mostly unchanged for over 200 years. Common practitioner complaints include not being able to hear sounds clearly due to ambient noise, frequent misplacement, and high costs associated with digital alternatives. Although digital stethoscopes are available on the market, they have not seen widespread adoption, largely due to their costs often exceeding $300.
Our objective is to design and build an affordable, digital smart stethoscope that enhances the user experience for healthcare professionals while addressing the limitations of traditional models. The system will include both the hardware device and a companion mobile application that enables real-time visualization and playback of heart and lung sounds.

### Project Approach

The final goal of building a digital stethoscope can be divided into three parts: hardware development, data acquisition and communication, and interface development.
Hardware Development will entail designing the embedded system that will acquire the heart and lung sounds and transmit them to the user interface. This will first require choosing a microcontroller that is able to communicate via Bluetooth or WiFi, process incoming audio signal data, and is

1

well documented to enable efficient setup. This will be done by researching a set of popular microcontrollers and evaluating these key requirements via a selection matrix. Once a microcontroller is selected, a microphone is needed to acquire heart and lung sounds. The requirements for the microphone are related to the frequency range of the sounds the product must acquire, which range between 20-4000 Hz. Additionally, the microphone must be able to interface with the selected microcontroller. Once some options are identified, they will be tested and compared for quality and ability to capture heart and lung sounds. To further improve the acquisition of audio signals, noise insulating materials will be used in conjunction with the microphone. Several foam and noise insulating materials will be tested to determine the best method to improve the audio acquired. Once these components are finalized, the final casing of the product will be designed and printed. The ergonomics and ruggedness of the casing will be tested to withstand the wear and tear expected in an urgent care setting.
Data Acquisition and Communication will require interfacing with the microphone directly from the microcontroller to record audio data. The first step will be to pull basic audio from the microphone and read it through the Serial Monitor interface of the microcontroller. Once this can be done reliably, the quality of the audio will be improved by testing different filtering approaches along with testing different acquisition settings including sample rate. The next step will be to set up a reliable method to communicate a fixed-length audio file. This will be tested on both WiFi and Bluetooth to determine the best approach to communicating the data.
Interface development is related to the user interface and experience. A test application with basic functionality will be deployed as a first step. From here, features will be added in an iterative fashion to allow users to playback audio, attach audio to patients, and seamlessly navigate the interface to find previous recordings. These features will be tested using unit and integration testing. A backend will be set up to store audio data received from the hardware device in an efficient manner to serve users when requested.

### Minimum Viable Product

The goal of our Minimum Viable Product (MVP) is to develop a fully functional and portable digital stethoscope that captures, amplifies, records, and visualizes heart and lung sounds. This MVP serves as a proof-of-concept, providing the foundational system architecture for our broader vision while

2

allowing us to gather early user feedback and iterate over time. Our emphasis is on deliverability: each core function is selected for high feasibility and clear alignment with the project’s long-term clinical goals.

Core MVP Components

1. Acoustic Signal Acquisition: The MVP will use a digital microphone with sensitivity in the appropriate frequency bands for heart and lung sounds. The system will be integrated into a robust enclosure modeled after existing stethoscope chest pieces to facilitate familiarity and ergonomics.
2. Recording and Playback: The MVP must reliably capture sound data for local storage and enable playback through either a speaker or through the front end software interface. Data will be stored securely and labeled with timestamps, creating a foundation for potential clinical documentation or further diagnostic analysis.
3. Portable and Durable Hardware Design: The stethoscope will be encased in a 3D-printed shell that is both lightweight and resilient. It will house the microcontroller, power supply (battery), and microphone. The prototype will prioritize modularity to support future iterations, such as integration of custom PCBs or embedded ML components.
4. Visualization via Companion Interface: The MVP will include a simple user interface (UI) that visualizes the sound waveform and increases the sound captured by the device. This UI will be implemented either as a mobile app based on preliminary user research and will focus on clarity and usability. The visualization and audio allows real-time signal monitoring, enabling both users and potential clinical testers to assess stethoscope performance.

The MVP is intentionally narrow in scope but complete in functionality. Each feature is selected to highlight a critical part of the user experience and overall system integrity. The emphasis is not on completeness or polish but on creating an end-to-end experience that can be tested, validated, and iterated upon. By grounding the MVP in core biomedical functionality (amplification, recording, and visualization), we create a minimum usable product that is meaningful to stakeholders and can evolve based on feedback.

3

The MVP enables us to evaluate core assumptions about hardware compatibility, UI requirements, and clinical relevance before committing to more complex features such as headphone integration, HIPAA compliance, edge ML deployment, or custom PCB creation. It also provides an anchor for testing usability, sound quality, and data handling practices early in the development lifecycle. Ultimately, our MVP will demonstrate that a portable, secure, and intelligible digital stethoscope can serve as a launchpad for more advanced diagnostic tools and integration with health information systems.

### Constraints, Risk, Feasibility

Developing a fully functional and portable digital stethoscope within a single quarter poses several technical constraints and risks that may deliver or prevent delivery. The most critical are summarized below:

1. Signal clarity and audio quality: Heart and lung sounds are lowamplitude and easily obscured by background noise, or mechanical interference. Given the limited time available for analog circuit tuning, we may encounter issues with poor amplification or noise recordings that render the audio useless to the target user. To mitigate this, we will prioritize selecting a high-sensitivity, low-frequency microphone early in our development. We may also incorporate lightweight digital filters, if necessary. We will also conduct early testing under realistic noise conditions to evaluate system performance, and give us time to iterate on the design if needed.
2. Audio compression and audio processing: Microcontrollers have limited compute resources. Real-time digital signal processing or compression may exceed CPU or memory limits on them, resulting in latency, or degraded playback quality. Furthermore, lossy compression formats, like MP3, may eliminate subtle audio cues that are important to clinicians. To reduce these risks, we will store audio in a lossless format, such as WAV. Heavier signal processing and compression will be offloaded to the mobile application or deferred until after recording.
3. Hardware design complexity: The system must combine components such as a microphone, power supply, and microcontroller in a portable form. Therefore, integration issues, like signal degradation,

4

power instability, or physical interference are possible, and can be timeconsuming to find and resolve. To minimize this risk, we will adopt a modular design approach that enables us to test individual components before full integration. We will also allocate buffer time for debugging and ensure proper shielding,grounding and circuit layout in the hardware design.

4. Data Transmission from Device to iOS App: Data transmission is likely the biggest risk, as there are both hardware and software constraints involved. iOS imposes strict limits on supported Bluetooth profiles, so we are limited to Bluetooth Low Energy (BLE), which has a low data throughput and limited real-time transmission capabilities. This poses a challenge for transmitting high-fidelity audio. To address this issue, we can segment audio into BLE-compatible chunks with proper sequencing and buffering. Another option to keep recording intact, would be to use Wi-Fi transmission via a microcontroller-hosted local server.

## Group Management

To help divide up the work, we will be splitting the hardware and software aspects of the project into two teams, in which each team of two will work closely with one another to make progress toward each weekly milestone. Specific decisions about project direction and implementation details will be decided by group consensus.
We will primarily be communicating over text messaging to plan meetings and to get quick feedback from other members. We will be meeting in person on Tuesdays and Thursdays in-class, and additionally on Thursdays after class for a stand-up to communicate current progress and next steps. Some milestones that we have defined require that the teams work together, which we will plan for during our in-person Thursday meetings. Each team will coordinate to meet with each other outside of these times in-person or over Zoom. We will know if we are off-schedule if we do not meet the weekly milestone goals we have set. If we find ourselves in this position, we will identify the root of what is causing the delays and plan to catch up the following week.
We will reach out to class TAs and more experienced individuals like the

5

Makerspace to get past issues that are causing us to slow down our progress. This also may require us to prioritize certain features over others if they are not necessary for our MVP, which we will decide on as a group. The Gantt chart below provides a detailed breakdown of who is responsible for each milestone. Shelby and Siya will be working on the software side of the project, while Amrita and Shayan will work on the hardware side.

6

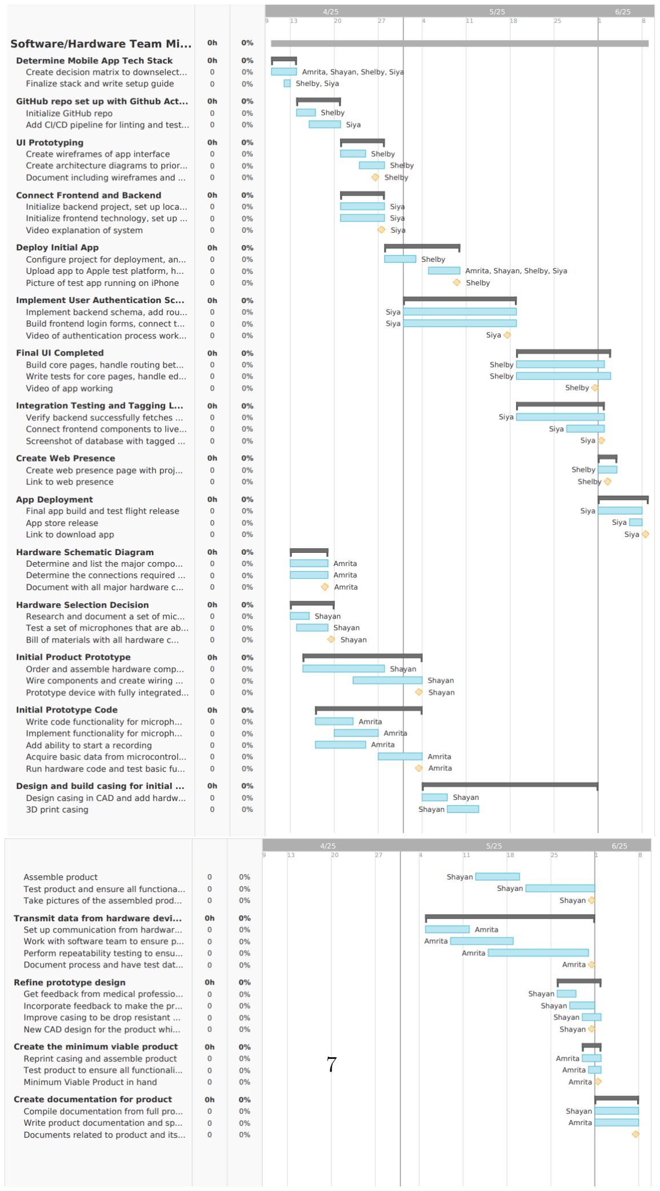
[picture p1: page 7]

7

## Project Development

The team will be split into hardware and software, with some overlap as the nature of the project requires all members to be fluid in their roles. The hardware team will primarily be Shayan and Amrita and the software team will be Shelby and Siya. Each team will work towards deliverables which will be assigned to specific individuals on the team.
The hardware needed for the project is likely a microcontroller like an ESP32, a digital MEMS microphone, various electrical components (resistors, capacitors, buttons, etc), and 3D printing materials. The team has most of this already ordered and available and can source the remaining parts from places like the UCSD Makerspace. The software used will be a backend database and Swift for the mobile application.
The hardware chosen are mostly commonly available components that are standard in hobby projects. These parts will be sourced from Amazon and some specialized electronics sites. The arrival time will likely be within a week. Software costs will likely relate to storage using a database service which is required given a data-centric project.
Hardware testing will be done through benchmarking and requirements testing. On the software side, unit and integration testing will be used to ensure a strong pipeline from the hardware all the way to the user facing application.
Documentation will be a priority that is done throughout the course of the project. Each week, the team will meet to summarize progress, setbacks, and lessons learned. Additionally, through the use of milestones and deliverables the team will have a meticulous record of each stage of the project from start to finish.

## Project Milestones and Schedule

### Hardware

- Deliverable 1 (Week 3): Hardware Schematic Diagram (Amrita)
Proof: Document with all major hardware components mapped out Milestones:

8

– Determine and list major components needed based on final product requirements

– Determine connections and additional interfacing components

- Deliverable 2 (Week 3): Hardware Selection Decision (Shayan) Proof: Bill of materials based on hardware schematic diagram Milestones:

– Research and downselect microcontrollers

– Test microphones for heart and lung sound frequencies

– Decide on filtering approach (analog and/or digital) to isolate target frequency bands for heart (typically 20–150 Hz) and lung (100–1000 Hz) sounds

- Deliverable 3 (Week 5): Initial Product Prototype (Shayan) Proof: Prototype with fully integrated hardware components Milestones:

– Order and assemble hardware

– Wire components, create documentation and diagram

- Deliverable 4 (Week 5): Initial Prototype Code (Amrita) Proof: Run and test hardware code, graphs showing frequency response before and after filtering, video demonstration
Milestones:

– Microphone data acquisition and processing

– Recording functionality

– Implement digital filtering to isolate relevant sound frequencies

– Transmit data from microcontroller to device

- Deliverable 5 (Week 7): Design and Build Casing (Shayan) Proof: Pictures of assembled product, tested with casing Milestones:

– CAD design, dimensioning and tolerancing

– 3D print and assemble casing

9

– Test full product functionality

- Deliverable 6 (Week 7): Transmit Data to Database (Amrita) Proof: Documented process with test data samples in database Milestones:

– Communication from device to external gateway

– Route data from gateway to database

– Repeatability testing to ensure consistency and quality

- Deliverable 7 (Week 9): Refine Prototype Design (Shayan) Proof: New CAD design focused on ruggedness and ergonomics Milestones:

– Feedback from medical professionals

– Improve usability, add drop and water resistance

- Deliverable 8 (Week 9): Create MVP (Amrita) Proof: MVP in hand
Milestones:

– Reprint casing, assemble product

– Full functionality testing

- Deliverable 9 (Week 10): Product Documentation (Shayan and Amrita)
Proof: Full documentation, specifications, and use cases
Milestones:

– Compile and write product documentation

– Specifications sheet with safety and use case info

### Software

- Deliverable 1 (Week 2): Tech Stack Decision (Shelby) Proof: Tech stack list and rationale
Milestones:

– Compare options and finalize stack

10

– Write setup guide

- Deliverable 2 (Week 2): GitHub Setup (Siya) Proof: Screenshot of repo and CI/CD pipeline Milestones:

– Initialize repo

– Add CI/CD for linting and testing

- Deliverable 3 (Week 4): UI Prototyping (Shelby) Proof: Wireframes and architecture document Milestones:

– Create Figma wireframes

– Diagram architecture for modularity

- Deliverable 4 (Week 4): Frontend and Backend Setup (Siya) Proof: Video explanation of system
Milestones:

– Backend init, sample route, local DB

– Frontend init and routing

- Deliverable 5 (Week 5): Deploying Test App (Shelby) Proof: Picture of test app on iPhone
Milestones:

– Configure deployment and fix permission issues

– Upload to Apple test platform and test usability

- Deliverable 6 (Week 5): Add Authentication (Siya) Proof: Video of working auth flow
Milestones:

– Backend schema and session logic

– Frontend login and API integration

- Deliverable 7 (Week 8): UI Complete (Shelby) Proof: App walkthrough video
Milestones:

11

– Build and route core pages

– Write tests and handle edge cases

- Deliverable 8 (Week 8): Integration Test + Tagging (Siya) Proof: Screenshot of database with tags
Milestones:

– Backend fetching and tagging

– Integrate simple waveform display for audio recordings

– Connect live frontend-backend and verify E2E

- Deliverable 9 (Week 10): Web Presence (Shelby) Proof: Link to website
Milestones:

– Create and deploy webpage

- Deliverable 10 (Week 10): App Deployment (Siya) Proof: Link to download app
Milestones:

– Final app build, TestFlight and App Store release

12

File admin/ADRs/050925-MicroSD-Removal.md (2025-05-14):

# Architecture Decision Record: Removal of microSD Dependency Using PSRAM

**Status**: Accepted  
**Date**: 2025-05-09

---

## 1. Context

Early iterations of our design used a microSD card for local storage of .wav audio files before uploading them to the Firebase database. While functional, this approach increased latency and required additional components and wiring and increased the likelihood of hardware-related failure. As testing progressed, the team discovered that the onboard 8MB PSRAM (pseudo-static RAM) on the ESP32-S3 module could be enabled and used to store temporary recording data, making the SD card unnecessary for the current file size requirements.
## 2. Decision

Our team removed the need for a microSD card by using PSRAM.

## 3. Rationale

A 30-second .wav file is only ~2.6 MB, which fits within the 8MB limit for PSRAM. Memory-based storage also enables faster access and avoids file write delays that could lead to timing issues during recording.

## 4. Consequences

### Positive outcomes

- Upload now takes ~20 seconds with PSRAM-based storage as opposed to about 60-90 seconds from end of recording.
- Entire audio pipeline now completes in ~45–50 seconds, including 30 seconds for recording.
- Pre-allocating the buffer removed a costly memory operation, improving efficiency.

### Negative outcomes
- Limited by total available PSRAM (future stretch goals may exceed this buffer)
- Removed flexibility to retain multiple files locally if needed

### Changes to systems/processes
- Firmware now initializes a global buffer in setup() for audio capture

- No need to delete files post-upload as we had to with the microSD card

## 5. Alternatives Considered

N/A

## 6. References

Support for External RAM [https://docs.espressif.com/projects/esp-idf/en/stable/esp32/api-guides/external-ram.html]

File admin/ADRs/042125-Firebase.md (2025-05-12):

# Architecture Decision Record: Use of Firebase for Authentication and Firestore Database

**Status**: Accepted  
**Date**: 04-21-25 

---

## 1. Context

We are developing a digital stethoscope system that captures `.wav` audio recordings from a custom hardware device and makes them accessible to users via a mobile or web application. To support this system, we require a backend that can:

- Receive and store `.wav` files (directly from the device)
- Associate each file with relevant metadata (e.g., user ID, timestamp)
- Securely manage user accounts and control access to data
- Provide real-time data access and synchronization to the app

Our goal is to keep the backend simple, scalable, and tightly integrated with our app development workflow.

## 2. Decision

We have chosen to use **Firebase** for the backend, specifically:

- **Firebase Authentication** to handle user sign-in, identity management, and access control.
- **Cloud Firestore** to store `.wav` audio files and associated metadata, enabling real-time syncing with the frontend.

## 3. Rationale

Firebase offers several benefits that align well with our project goals:

- **Tight integration** with mobile/web apps via official SDKs
- **Real-time updates** using Firestore, which is important for synchronizing recordings as they are uploaded
- **Authentication built-in**, reducing the need to implement a separate user management system
- **Managed infrastructure**, allowing us to focus on building the application rather than maintaining servers
- **Security rules** in Firestore and Firebase Auth ensure that users only access their own data

Although Firestore is not traditionally optimized for large file storage, our early-stage prototype uses it to store `.wav` files (e.g., as binary blobs or base64 strings) for simplicity.

## 4. Consequences

**Positive outcomes:**
- Rapid development with minimal backend code
- Real-time data access in the app
- Centralized and secure user authentication
- Scalable infrastructure with low maintenance overhead

**Negative outcomes:**
- Firestore is not optimized for large binary data, which may impact performance or cost at scale

## 5. Alternatives Considered

- **Firebase + Cloud Storage**: More appropriate for binary files, but introduces added complexity for now.
- **AWS (S3 + Cognito + DynamoDB)**: Powerful and flexible but requires more setup and integration effort.

## 6. Related Decisions

- Future ADR may be needed if we decide to offload audio file storage to a more suitable system.

## 7. References

- [Firebase Authentication](https://firebase.google.com/products/auth)
- [Cloud Firestore](https://firebase.google.com/products/firestore)

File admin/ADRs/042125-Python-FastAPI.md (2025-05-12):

# Architecture Decision Record: Use of Python and FastAPI for Backend Development

**Status**: Accepted  
**Date**: 04-21-25 

---

## 1. Context

As part of our digital stethoscope system, we require a backend to support a variety of services including device communication, data processing, and integration with our frontend application. This backend must be lightweight, fast, easy to develop and maintain, and suitable for handling future data-intensive tasks such as audio analysis and machine learning.

Our team considered several backend technologies across different languages and frameworks before selecting a final stack.

## 2. Decision

We have chosen to build our backend using **Python** with the **FastAPI** framework.

## 3. Rationale

FastAPI and Python offer a strong combination of developer speed, performance, and extensibility, particularly given our current and future needs:

- **Developer familiarity**: Python is a widely known and accessible language for our team, enabling rapid development and iteration.
- **Performance**: FastAPI is built on Starlette and uses asynchronous request handling (via `async/await`), making it fast enough for our use case.
- **Scalability**: The framework is lightweight and modular, making it easy to scale components independently as the system grows.
- **ML and audio processing readiness**: Since much of our potential data analysis and potential machine learning work will be in Python, it makes sense to keep the backend in the same ecosystem for smooth integration.
- **Community and ecosystem**: FastAPI has strong community support and is increasingly used in production systems.

## 4. Consequences

**Positive outcomes:**
- Rapid backend development and easy onboarding for new developers
- Clean, auto-documented API surface for frontend and hardware integration
- Aligned with future machine learning and audio processing pipelines
- Modular and scalable architecture

**Negative outcomes:**
- Python is not as performant as lower-level languages for high-throughput systems (though FastAPI mitigates this with async support)
- Deployment and concurrency need to be handled carefully
- Potential for tighter coupling to Python-based tooling in the long term

## 5. Alternatives Considered

- **Node.js with Express**: Popular and lightweight, but less aligned with our ML pipeline and developer expertise.
- **Django**: Too heavy and opinionated for our needs; we preferred the minimalism and flexibility of FastAPI.

## 6. Related Decisions

- Integration with Firebase for authentication and database (see Firebase ADR)
- Future ADR may cover containerization and deployment strategy (e.g., Docker + CI/CD pipeline)

## 7. References

- [FastAPI Documentation](https://fastapi.tiangolo.com/)
- [Pydantic Documentation](https://docs.pydantic.dev/)
- [Uvicorn ASGI Server](https://www.uvicorn.org/)

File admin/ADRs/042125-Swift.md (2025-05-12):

# Architecture Decision Record: Use of Swift and SwiftUI for Frontend Development

**Status**: Accepted  
**Date**: 04-21-25  

---

## 1. Context

As part of our digital stethoscope project, we need a user-facing application to allow healthcare professionals to access and interact with audio recordings. The frontend must be intuitive, responsive, and designed with the needs of our target users in mind—primarily doctors and nurses working in clinical settings.

We evaluated different frontend technologies and platforms, including web apps and cross-platform frameworks. Our goal was to select a technology that aligns with both user preferences and our team’s ability to deliver a high-quality experience.

## 2. Decision

We have decided to build our frontend application using **Swift** and **SwiftUI**, targeting **iOS** devices.

## 3. Rationale

Our decision is based on both technical and user-centered factors:

- **User preference**: Through user research and interviews, we found that doctors and nurses strongly prefer using a **mobile app** on their **iPhone** over a web-based interface. They cited convenience, performance, and integration with their mobile workflow as key reasons.
- **Native performance**: Swift and SwiftUI provide smooth, fast, and responsive experiences, which is critical for applications that play and manage audio recordings.
- **Modern UI development**: SwiftUI allows for faster development with declarative syntax, built-in accessibility, and seamless integration with Apple design patterns.

## 4. Consequences

**Positive outcomes:**
- Delivers a polished, native user experience aligned with user expectations
- Simplifies UI development with SwiftUI’s declarative approach
- Leverages iOS system features and hardware for audio playback and secure data access
- Increases user trust and adoption by offering an experience that feels "professional" and reliable

**Negative outcomes:**
- Limits app availability to iOS devices (at least initially)
- We have not used Swift and SwiftUI, so there will be a learning curve for our software team
- Android support will require a separate codebase if/when needed

## 5. Alternatives Considered

- **Web app**: Rejected based on user feedback—clinical users preferred native mobile apps due to better usability and performance on phones.
- **React Native / Flutter**: Considered for cross-platform development, but we prioritized native performance and UI fidelity over cross-platform reach.

## 6. Related Decisions

- See ADR on Firebase for how the app integrates with authentication and Firestore.
- A future ADR may address cross-platform expansion, including Android.

## 7. References

- [SwiftUI Overview](https://developer.apple.com/xcode/swiftui/)
- [Apple Human Interface Guidelines](https://developer.apple.com/design/human-interface-guidelines/)

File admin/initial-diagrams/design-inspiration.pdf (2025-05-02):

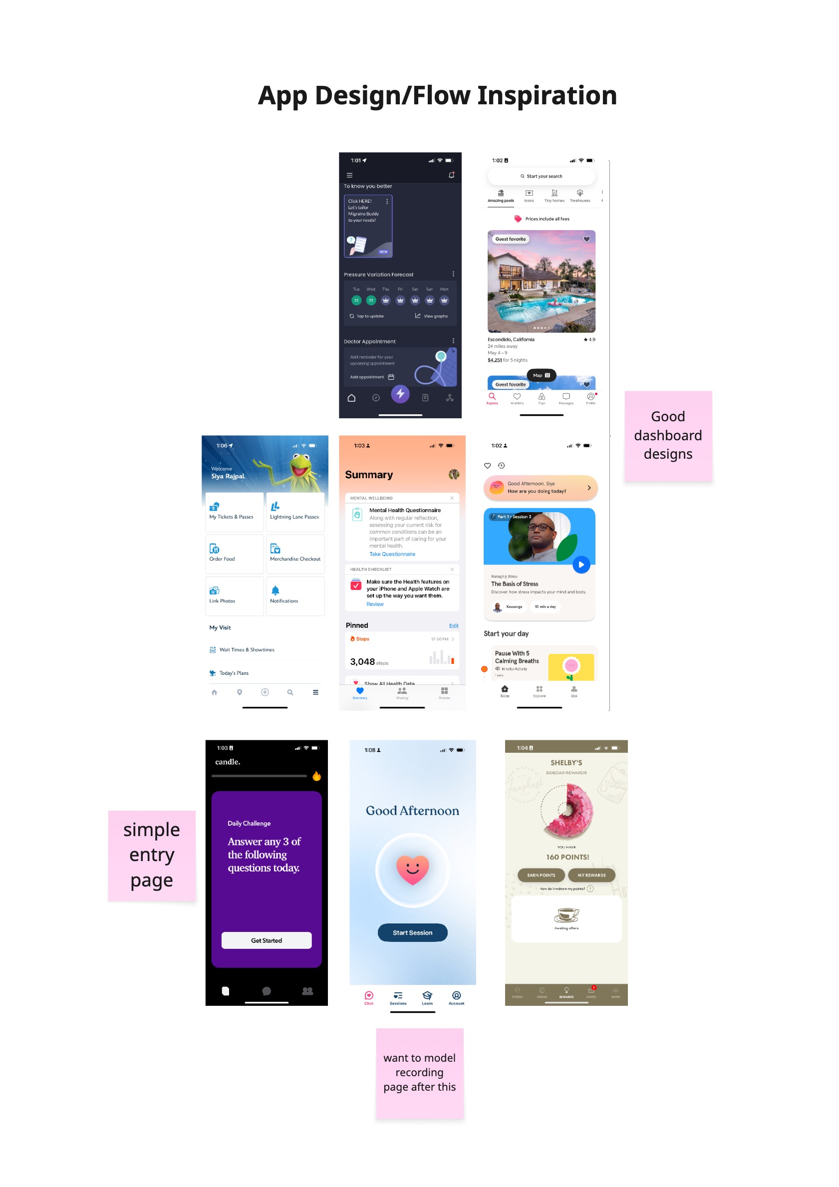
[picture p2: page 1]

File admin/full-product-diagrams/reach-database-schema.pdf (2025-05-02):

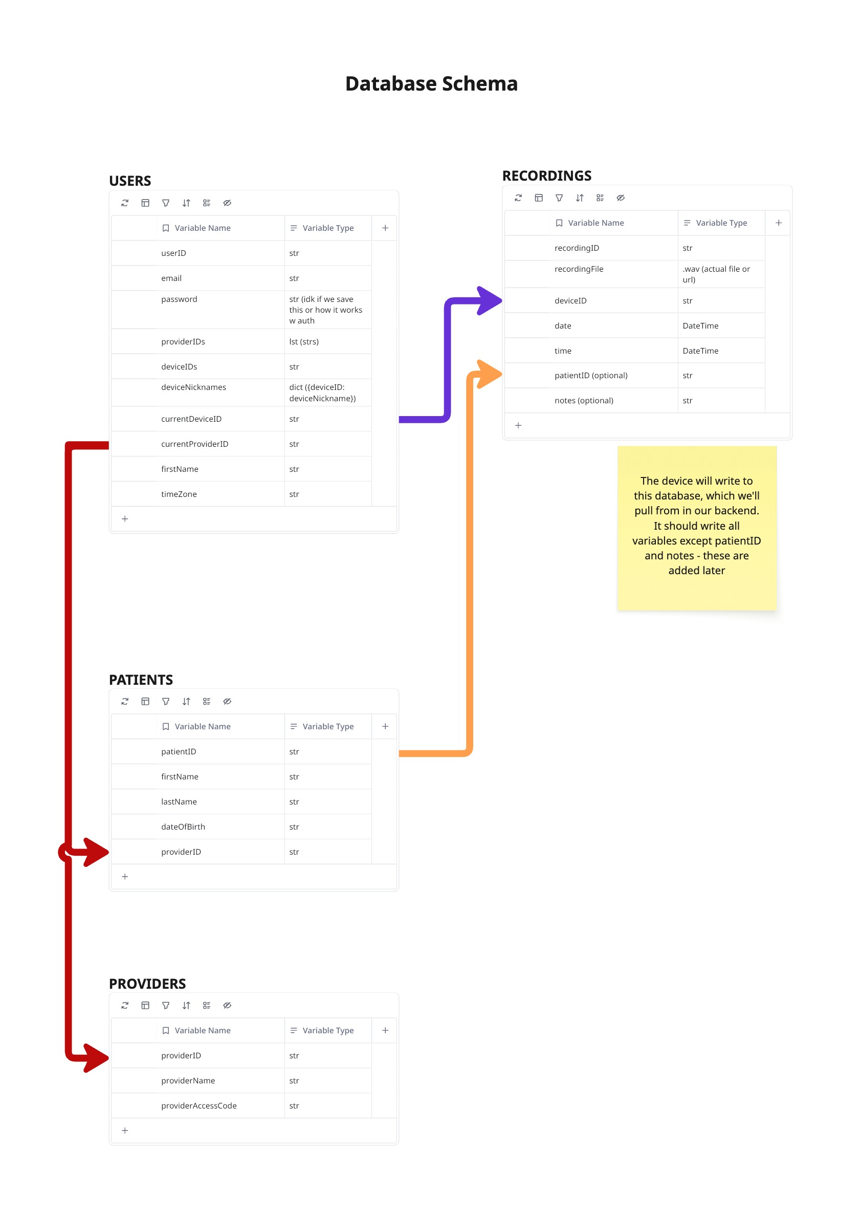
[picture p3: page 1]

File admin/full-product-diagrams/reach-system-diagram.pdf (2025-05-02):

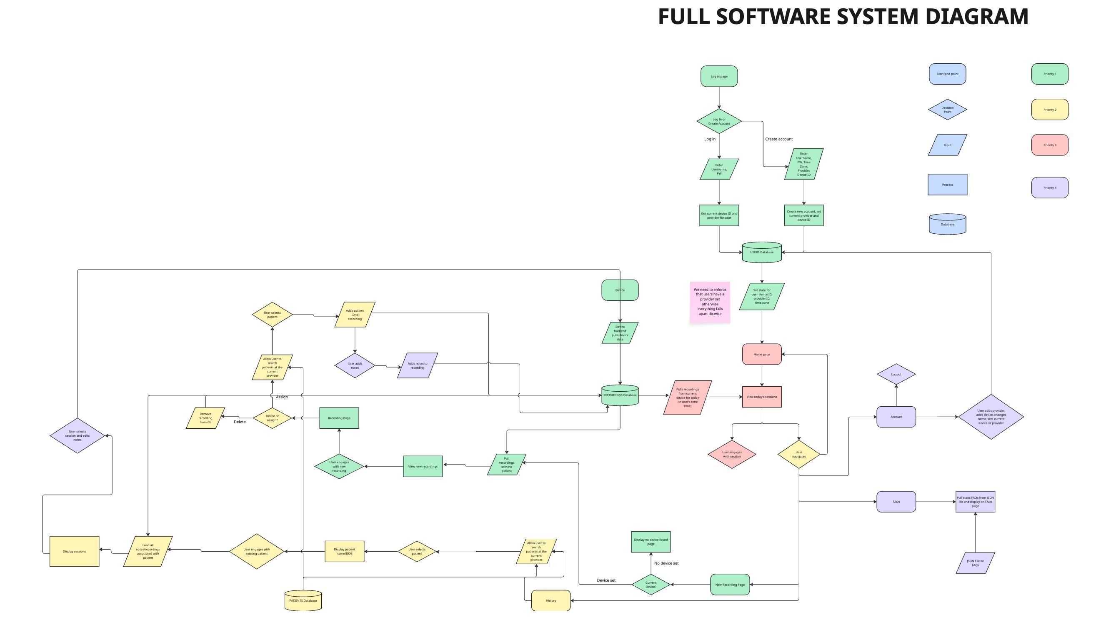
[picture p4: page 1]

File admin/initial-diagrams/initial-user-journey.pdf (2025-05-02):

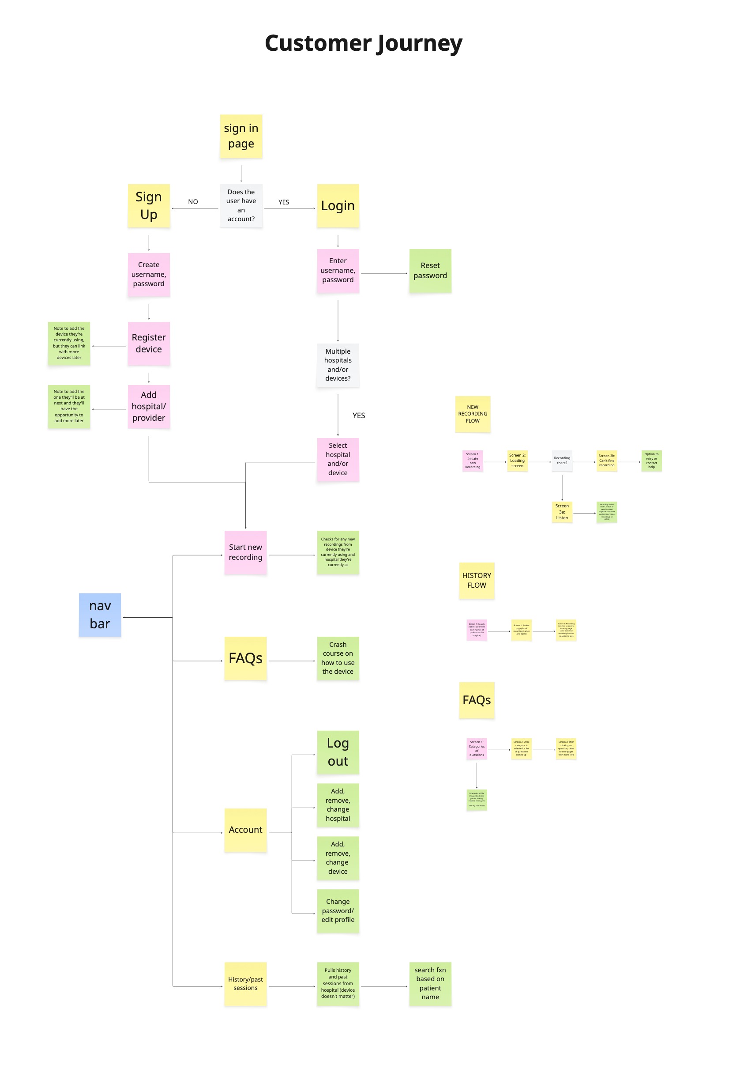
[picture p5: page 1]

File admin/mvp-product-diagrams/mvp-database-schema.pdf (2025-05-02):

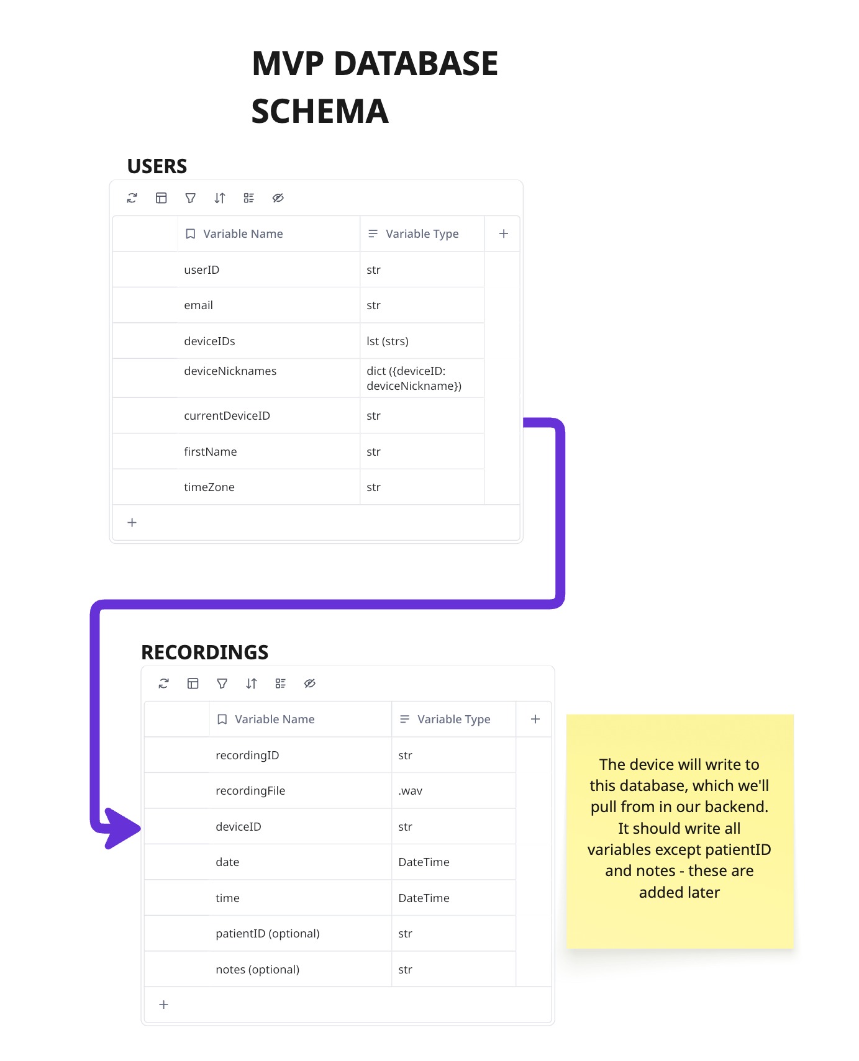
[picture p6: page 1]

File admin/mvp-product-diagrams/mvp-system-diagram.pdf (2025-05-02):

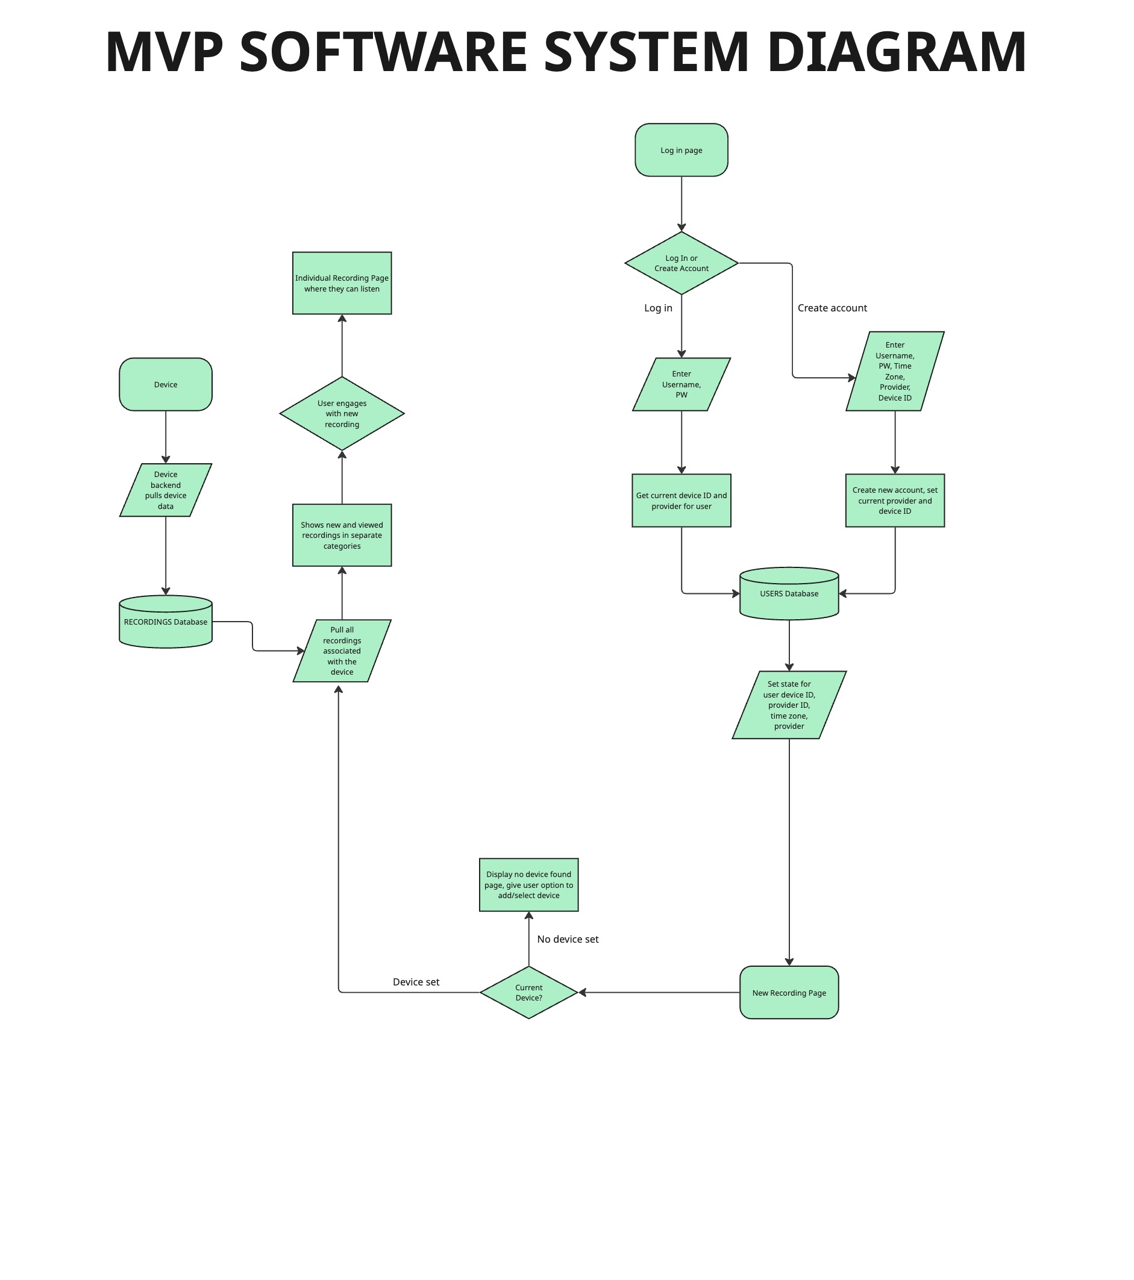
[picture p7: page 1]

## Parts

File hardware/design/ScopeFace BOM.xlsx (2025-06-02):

Part | Quantity | Unit Cost | Amount | Source
XIAO ESP32-S3 | 1 | $16.99 | $16.99 | link (https://www.amazon.com/dp/B0BYSB66S5?ref=ppx_yo2ov_dt_b_fed_asin_title)
3.7V Lipo Battery 350mAh | 1 | $7.99 | $7.99 | link (https://www.amazon.com/dp/B0CNLNXTZ5?ref=ppx_yo2ov_dt_b_fed_asin_title&th=1)
Stethoscope Diaphragm Cover | 1 | $8.99 | $8.99 | link (https://www.amazon.com/Stethoscope-Replacement-Pediatric-Diaphragm-Accessories/dp/B08K2DTGV7?s=industrial)
JST-PH 2.0 Male and Female Connector Cable for Battery | 1 | $6.99 | $6.99 | link (https://www.amazon.com/dp/B07NWD5NTN?ref=ppx_yo2ov_dt_b_fed_asin_title)
Momentary Push Button | 1 | $8.99 | $8.99 | link (https://www.amazon.com/dp/B0DMVLJGDL?ref=ppx_yo2ov_dt_b_fed_asin_title&th=1)
M2 x 12mm | 1 | $7.76 | $7.76 | link (https://www.amazon.com/dp/B0D4JMTFLT?ref=ppx_yo2ov_dt_b_fed_asin_title)
Heated Threaded Inserts | 1 | $22.41 | $22.41 | link (https://www.mcmaster.com/nav/enter.asp?partnum=94180A312)
M2 x 25mm | 1 | $9.31 | $9.31 | link (https://www.mcmaster.com/nav/enter.asp?partnum=92010A111)
Microphone Evaluation Board | 1 | $2.66 | $2.66 | link (https://www.digikey.com/en/products/detail/pui-audio-inc/DMM-4026-B-I2S-R/11587483)
Common Anode LED | 1 | $2.25 | $2.25 | link (https://www.sparkfun.com/led-rgb-diffused-common-anode.html)
 |  | Total | $94.34

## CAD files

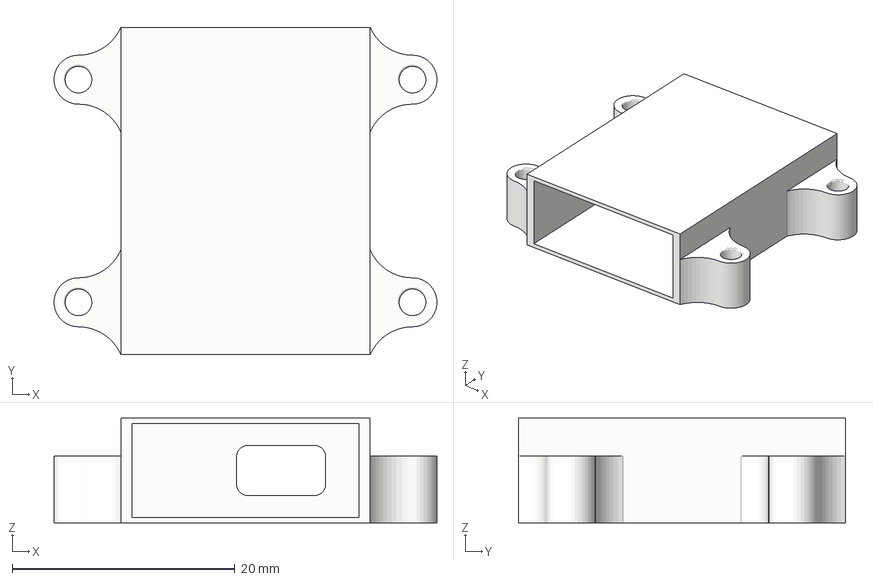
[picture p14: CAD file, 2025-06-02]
hardware/design/printing-files/Battery Holder.3mf
34.4 x 29.4 x 9.40 mm

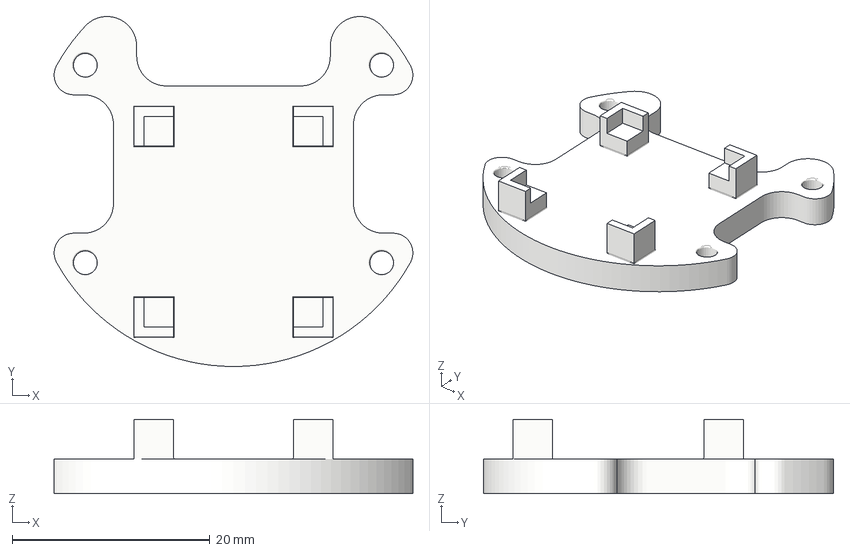
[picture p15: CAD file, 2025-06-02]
hardware/design/printing-files/ESP32 Mounting Plate.3mf
36.3 x 35.4 x 7.50 mm

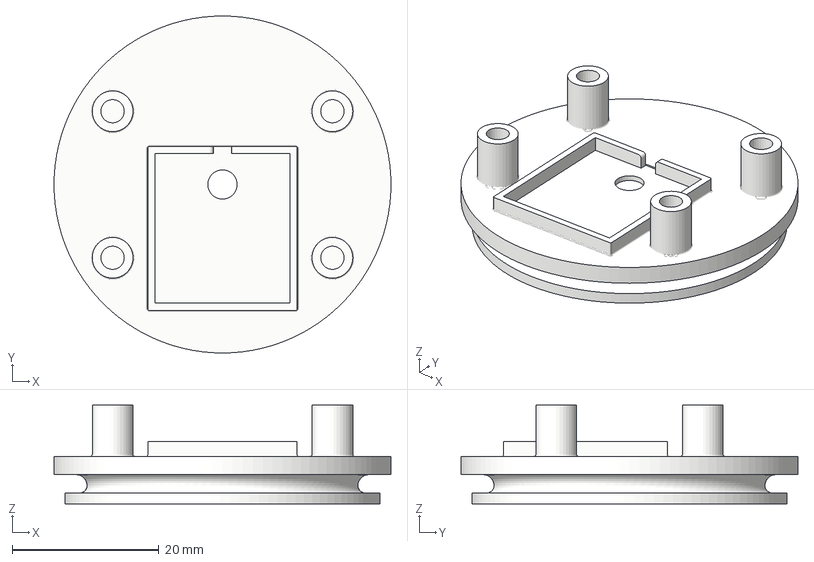
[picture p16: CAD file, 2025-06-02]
hardware/design/printing-files/Mic and Diaphragm Mount.3mf
46.0 x 46.0 x 13.5 mm

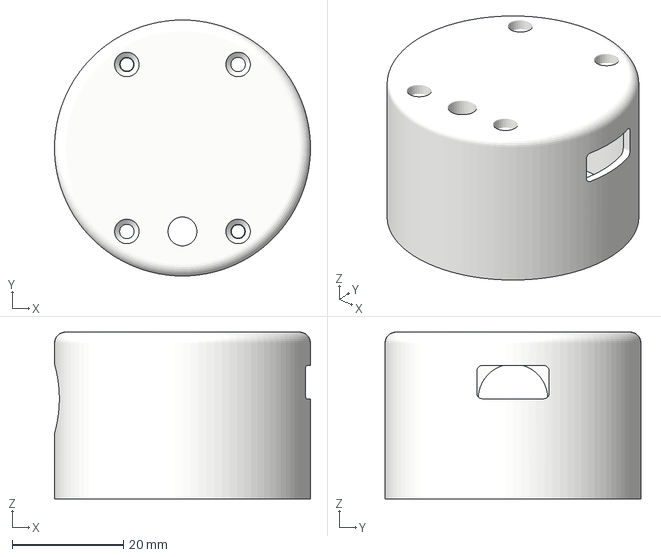
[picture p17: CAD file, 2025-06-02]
hardware/design/printing-files/Casing Cover.3mf
46.0 x 46.0 x 30.0 mm

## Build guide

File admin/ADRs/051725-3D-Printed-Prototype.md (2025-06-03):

# Architecture Decision Record: [Use of 3D Printing for Device Enclosure]

**Status**: [Accepted] 
**Date**: [2025-05-17]  

---

## 1. Context

The design requires mechanical stability and access to GPIO features (e.g., button, RGB diode). We explored manufacturing options for producing a suitable casing, including 3D printing, injection molding, and metal machining.

During this phase of development, we are rapidly iterating on layout, sizing, and component placement. A CAD model of the initial design was created and tested as part of the integrated pipeline.
## 2. Decision

We decided to 3D print the device enclosure using PETG material for prototyping and testing phases. We also tested PLA filaments.

## 3. Rationale

3D printing was selected over other manufacturing methods due to the following considerations:

Rapid iteration: Enables fast and low-cost turnaround for modifying and testing updated CAD models

Low upfront cost: Unlike injection molding or CNC machining, 3D printing does not require expensive tooling, molds, or setup costs.

Customizability: Easy to adapt design features such as button slots, microcontroller mounts, and access ports across iterations.

In-house fabrication: Printing can be done directly in our lab and the Envision Lab without relying on external vendors.

## 4. Consequences

Positive outcomes:

- Enables iterative mechanical testing with minimal delay.

- Simplifies integration of electronic components in a confined space.

Negative outcomes:

- Inconsistent print quality between different 3D printers and filament types can result in slight dimensional variances, affecting part fit and assembly precision.

- PETG material is less durable and heat-resistant than final production materials.

- Printed parts may not provide long-term mechanical stability or tight tolerances.

- Not suitable for final clinical-grade production without redesign.

## 5. Alternatives Considered

Injection molding: Rejected due to high upfront tooling cost and long lead times. Not suitable for frequent design changes at this stage.

Metal machining: Considered too rigid for rapid iteration. Also more expensive for early-stage prototype.

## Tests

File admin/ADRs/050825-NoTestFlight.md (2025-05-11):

# Architecture Decision Record: Avoid Use of TestFlight for Demo

**Status**: Accepted  
**Date**: 05-08-25

---

## 1. Context

As part of the development process for our iOS application, we explored methods to share app builds with team members and for demos. One standard option for distributing pre-release iOS applications is Apple's TestFlight platform. However, using TestFlight requires enrollment in the Apple Developer Program, which costs $99 USD per year.

We are currently operating with limited budget and resources, so we're evaluating cost-effective ways to demonstrate app functionality during early development stages.

## 2. Decision

We have decided **not** to use TestFlight for distributing demo builds of our iOS application. Instead, we will conduct all demos using the Xcode simulator.

## 3. Rationale

The primary reason for this decision is financial: enrolling in the Apple Developer Program solely to use TestFlight is not justified at this stage of the project. Since we do not need to test the app on physical devices yet, the Xcode simulator is sufficient for demonstrating basic functionality and UI to stakeholders.

Key factors considered:
- The $99/year Apple Developer fee
- The current need is limited to internal demos, not wide distribution or testing
- The Xcode simulator provides adequate functionality for early-stage demonstrations

## 4. Consequences

**Positive outcomes:**
- No immediate cost for developer account enrollment
- Simple and fast demo setup via simulator
- No need to manage provisioning profiles or UDIDs

**Negative outcomes:**
- Cannot test performance or device-specific issues on real iPhone devices
- Will require future investment if we decide to move to real device testing or App Store distribution

**Process changes:**
- All demos will be conducted via screen sharing or in-person sessions using the Xcode simulator

## 5. Alternatives Considered

- **Using TestFlight**: Rejected due to cost and current lack of need for real device testing
- **Building and distributing .ipa files manually**: This would take time away from our more desirable nice-to-have features and still requires developer account provisioning

## 6. Related Decisions

N/A

## 7. References

- [Apple Developer Program](https://developer.apple.com/programs/)
- [TestFlight Overview - Apple Developer Documentation](https://developer.apple.com/testflight/)

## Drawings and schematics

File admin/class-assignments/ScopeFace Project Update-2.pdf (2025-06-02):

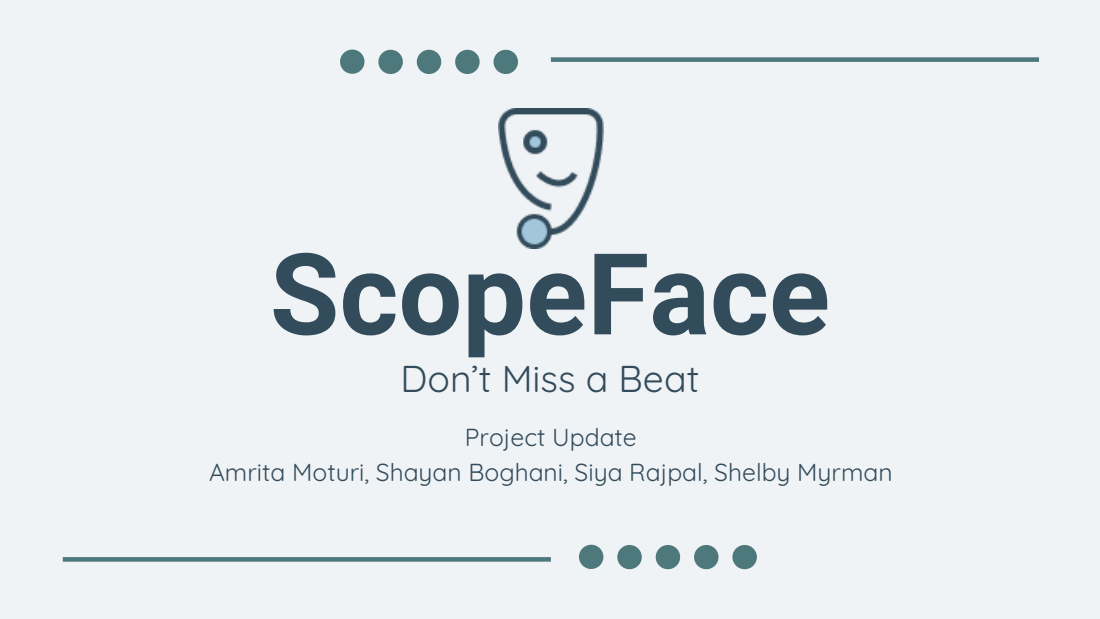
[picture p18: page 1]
ScopeFace; Project Update

Don’t Miss a Beat

Amrita Moturi, Shayan Boghani, Siya Rajpal, Shelby Myrman

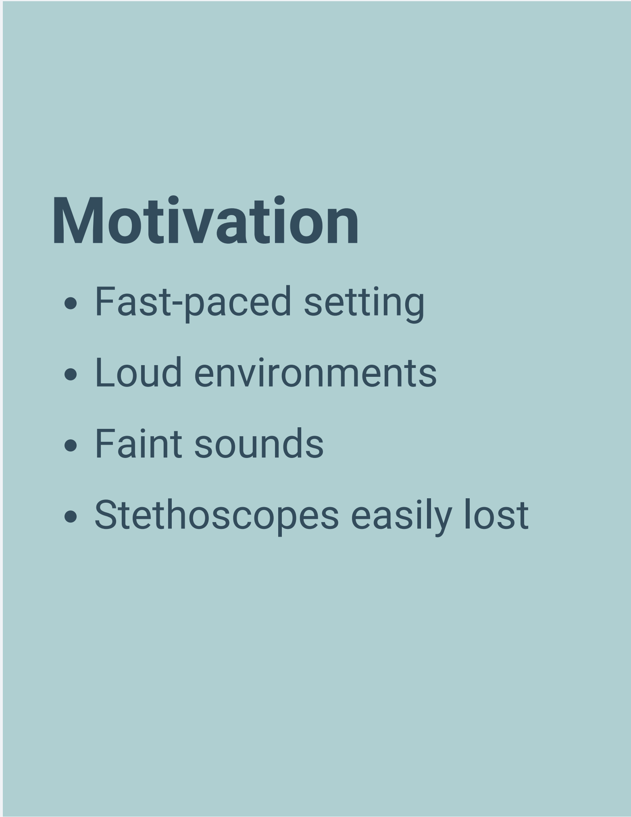
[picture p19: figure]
Motivation; Fast-paced setting; Loud environments; Faint sounds; Stethoscopes easily lost
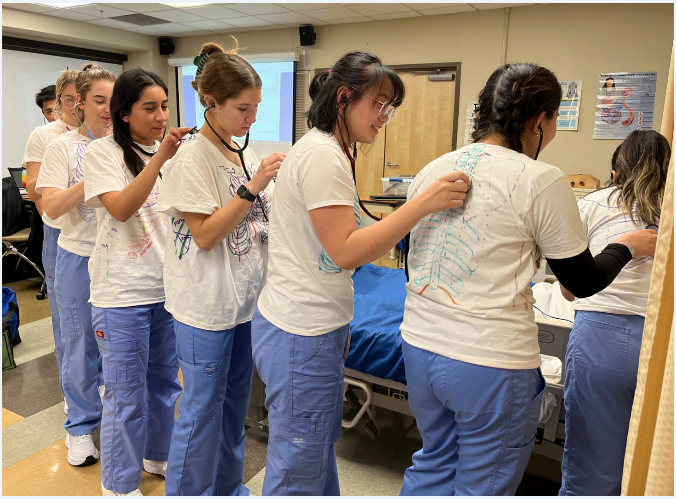
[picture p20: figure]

# Core Product

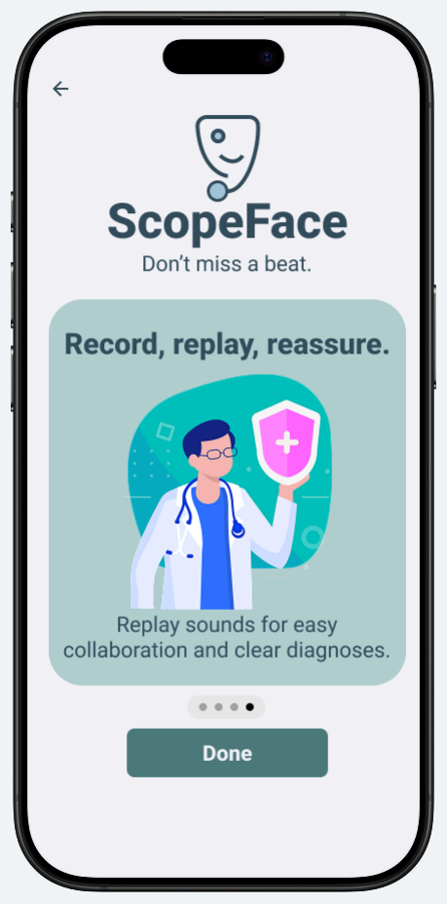
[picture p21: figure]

Acoustic signal acquisition and amplification
A portable and durable hardware design Visualization of heart and lung waveforms via companion app
In-app recording playback functionality

## Our MVP includes

# User Research

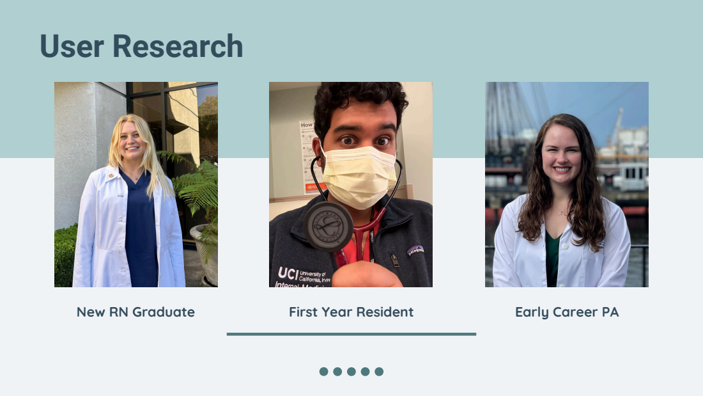
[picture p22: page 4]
New RN Graduate; First Year Resident; Early Career PA

# Full Software System Design

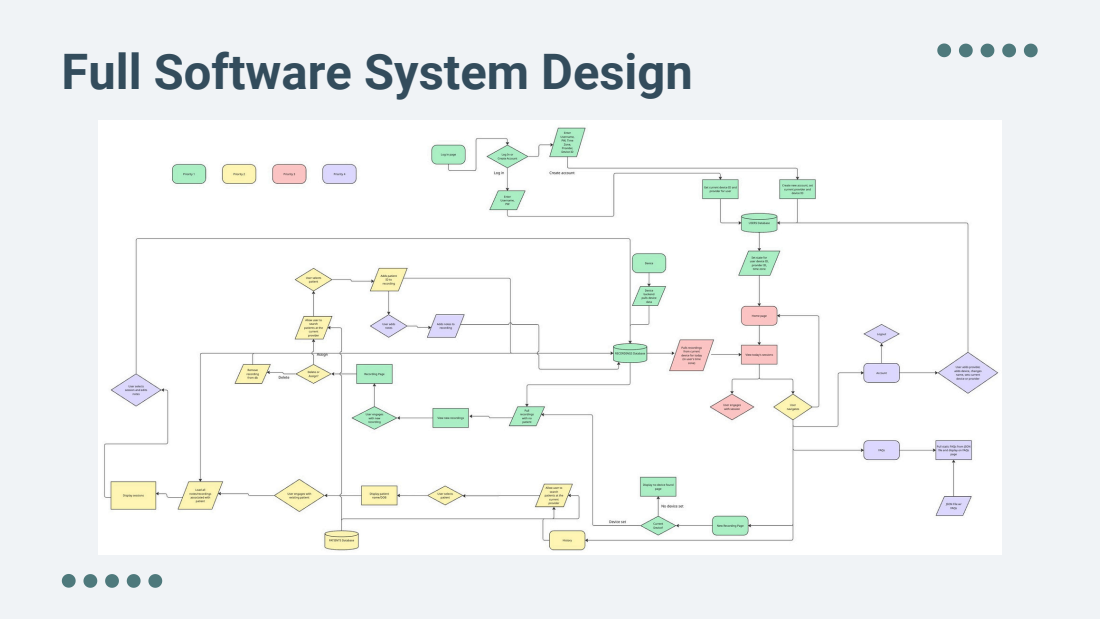
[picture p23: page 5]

# MVP Software System Design

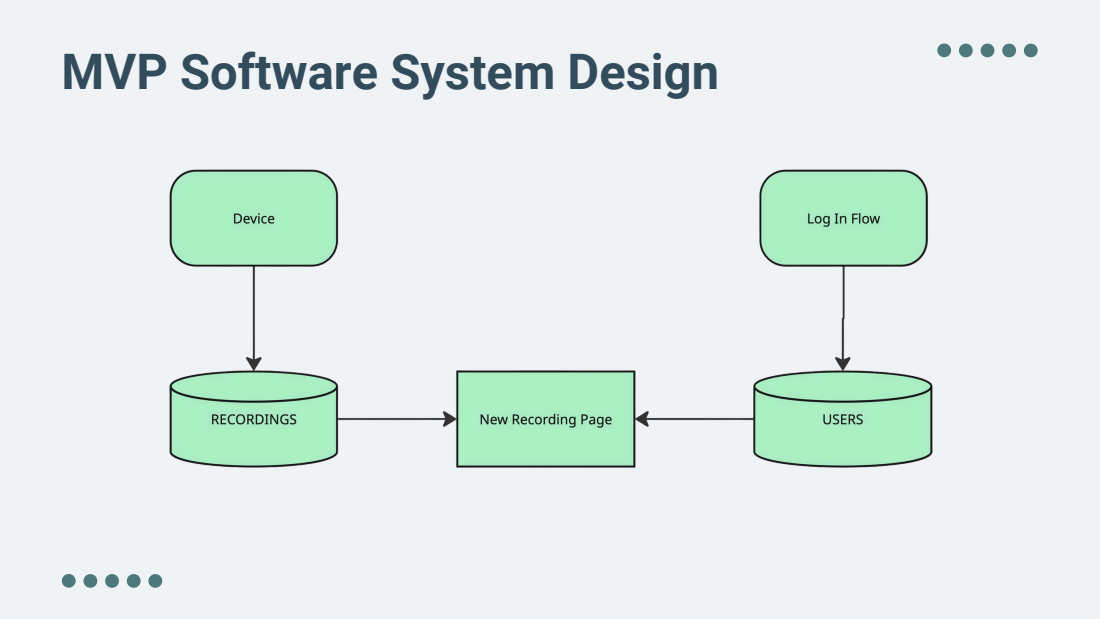
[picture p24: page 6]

# UI Prototypes & Authentication

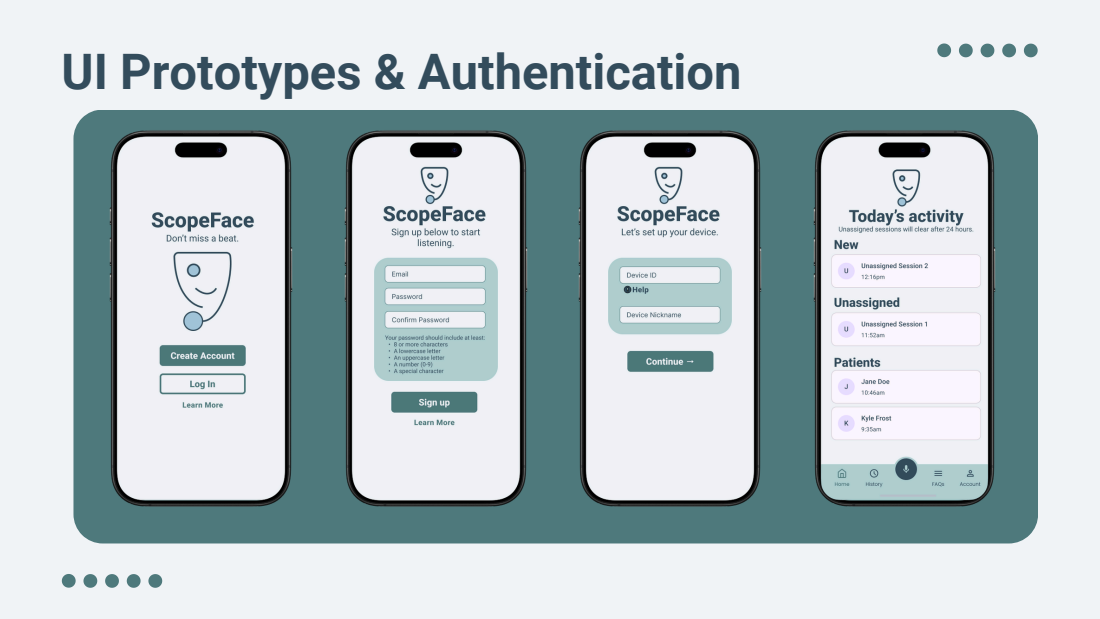
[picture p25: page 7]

# Hardware System Design

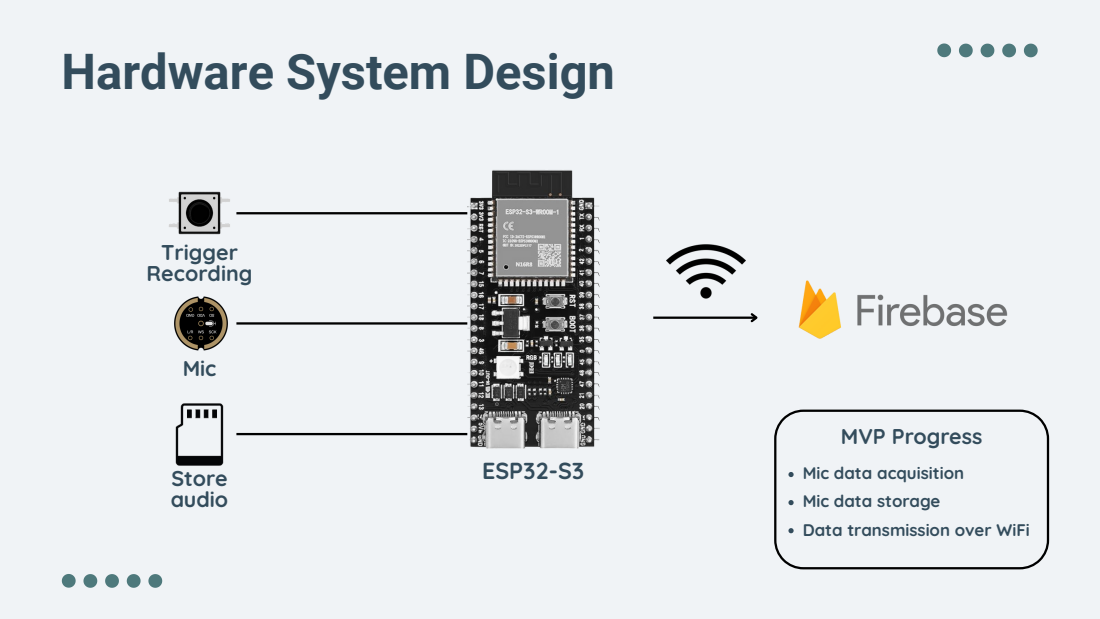
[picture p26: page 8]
ESP32-S3; Mic; Trigger Recording; Store audio; MVP Progress

Mic data acquisition
Mic data storage
Data transmission over WiFi

# Hardware Prototypes

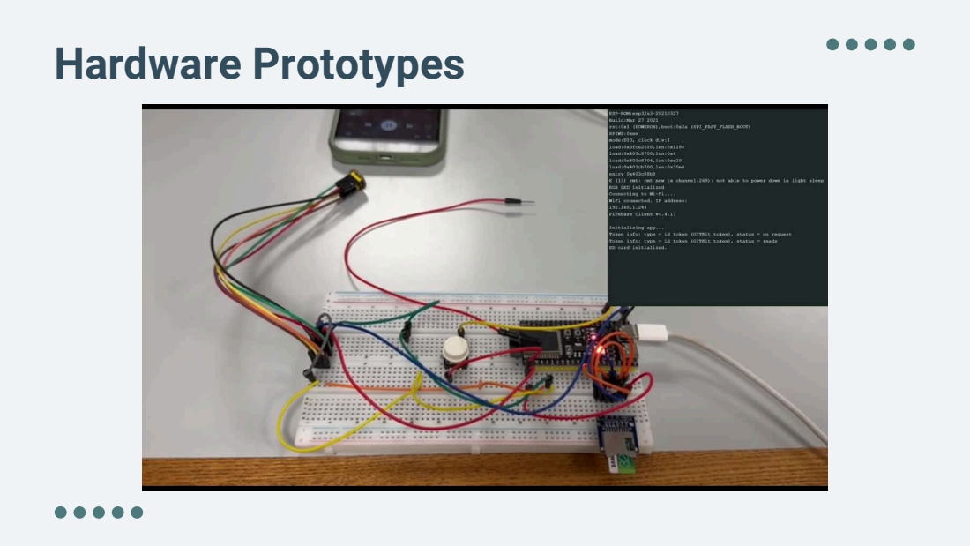
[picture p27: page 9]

# Next Steps: Software

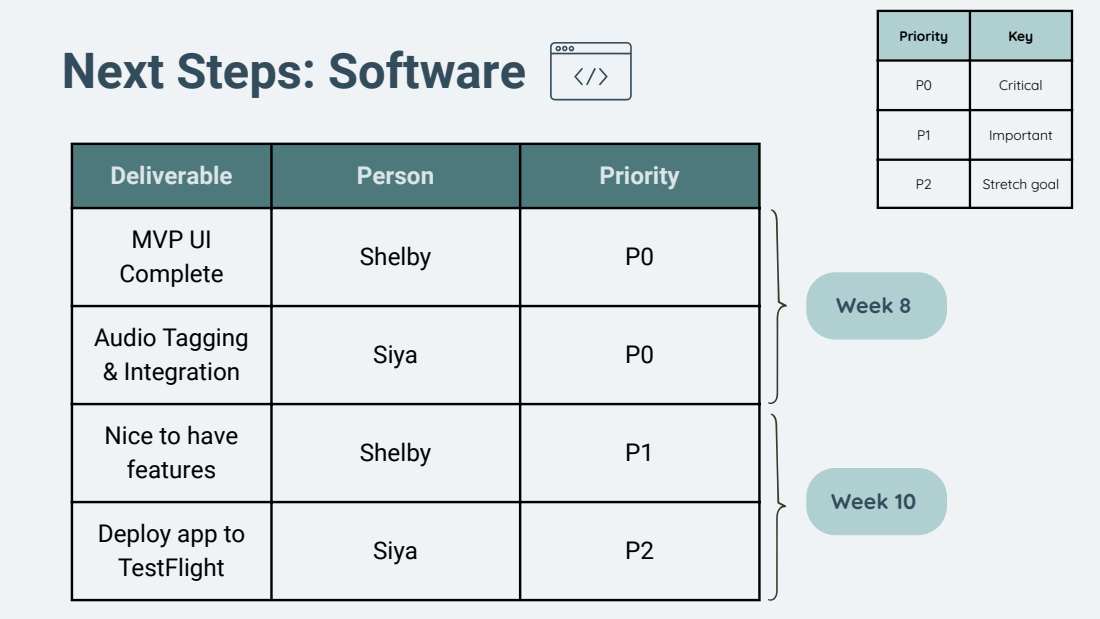
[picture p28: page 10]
Week 8; Week 10

Priority | Key

P0 | Critical

P1 | Important

Deliverable | Person | Priority

P2 | Stretch goal

MVP UI Complete | Shelby | P0

Audio Tagging & Integration | Siya | P0

Nice to have features | Shelby | P1

Deploy app to TestFlight | Siya | P2

# Next Steps: Hardware

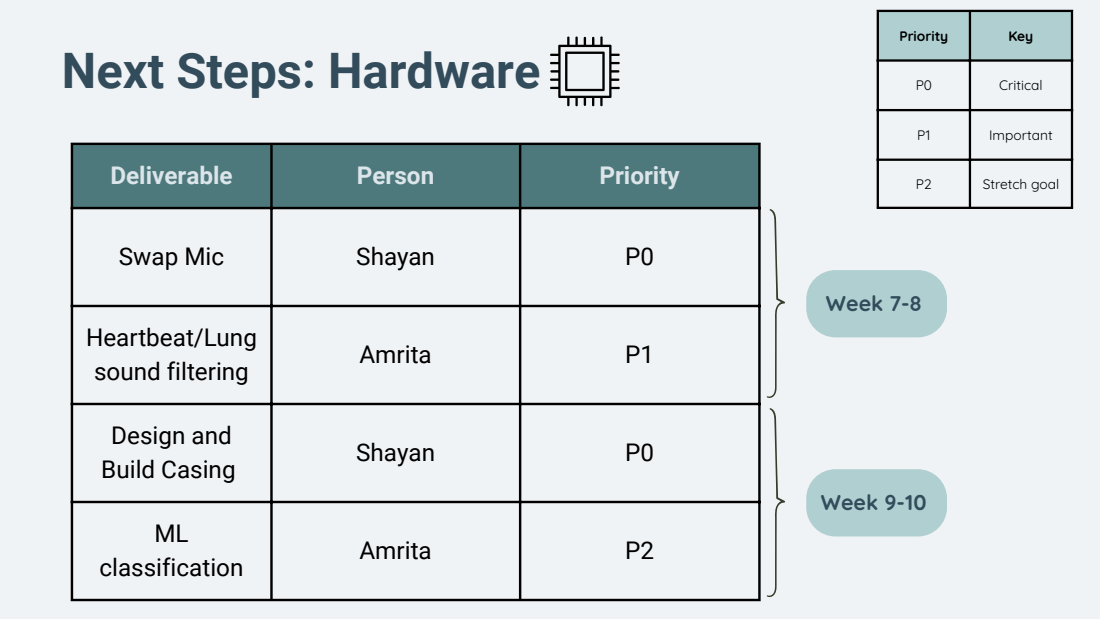
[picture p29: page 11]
Week 7-8; Week 9-10

Priority | Key

P0 | Critical

P1 | Important

Deliverable | Person | Priority

P2 | Stretch goal

Swap Mic | Shayan | P0

Heartbeat/Lung sound filtering | Amrita | P1

Design and Build Casing | Shayan | P0

ML classification | Amrita | P2

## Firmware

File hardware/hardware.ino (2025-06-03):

#include <Arduino.h>
#include <Firebase_ESP_Client.h>
#include <addons/TokenHelper.h>
#include <driver/i2s.h>
#include <WiFi.h>
//#include <esp_wpa2.h> // not needed unless using UCSD WiFi

/*
Pins for XIAO ESP32-S3
#define I2S_WS 6
#define I2S_SD 5
#define I2S_SCK 4
#define BUTTON_PIN 1

Internal LED
*/

/*
Don't forget to add back in these things when running code:

WiFi SSID
WiFi Password
API Key

Also, add in your authentication information:
- User Email
- User PW

If using UCSD WiFi:
- Uncomment include for esp_wpa2.h
- Uncomment WPA2 block
- Uncomment Enterprise WiFi initialization function (init_eduroam)
- Comment out code to initialize normal WiFi in setup
- Uncomment line to initialize Enterprise WiFi in setup
*/

// ------- Definitions and Constants -------

// ------- Pin Definitions -------
#define I2S_WS 6
#define I2S_SD 5
#define I2S_SCK 4
#define BUTTON_PIN 2
#define RED 9
#define GREEN 8

// ------- I2S Definitions and Constants -------
#define I2S_PORT I2S_NUM_0
#define BUFFER_LEN 512
#define RECORD_TIME 30
const uint32_t SAMPLE_RATE = 44100;
const uint16_t BITS_PER_SAMPLE = 16;
const uint16_t CHANNELS = 1;
const uint16_t WAV_HEADER_BYTES = 44;

const uint32_t AUDIO_BYTES = SAMPLE_RATE * RECORD_TIME * (BITS_PER_SAMPLE / 8);
const uint32_t TOTAL_BYTES = WAV_HEADER_BYTES + AUDIO_BYTES;

// ------- Deep Sleep Vars -------
unsigned long lastActiveTime = 0;
#define INACTIVITY_TIMEOUT (5 * 60 * 1000)  // 5 minutes in ms
#define WAKEUP_MASK 0X4 // GPIO Pin 2 so 2^2 in hex

// ------- WiFi Definitions -------

#define SSID "WIFI SSID"
#define wifiPW "PASSWORD"

/*
// not needed unless using UCSD WiFi (WPA2 Block)
#define EAP_IDENTITY "username@ucsd.edu"
#define EAP_USERNAME "username@ucsd.edu"
#define EAP_PASSWORD "YOUR PASSWORD HERE"
const char *ssid = "eduroam";
*/

// ------- Firebase Definitions and Initializations -------
#define API_KEY "API KEY HERE"
#define USER_EMAIL "stethy.mcscopeface@gmail.com"
#define USER_PW "scopeface237"
#define STORAGE_BUCKET "scopeface-10e9a.firebasestorage.app"

FirebaseData fbdo;
FirebaseAuth auth;
FirebaseConfig config;

// ------- Device Identifying Information
#define DEVICE_ID "s3asf017"

// ------- Global Variables -------
int16_t sBuffer[BUFFER_LEN];
uint8_t *wavBuffer = nullptr;
volatile bool startRecording = false;

// ------- Button Press Functionality -------
void IRAM_ATTR onButtonPress() {
  startRecording = true;
}

// ------- I2S Set Up Functions -------
/*
* This function installs the I2S protocol on the designated pins
*/
void i2s_install() {
  const i2s_config_t i2s_config = {
    .mode = (i2s_mode_t)(I2S_MODE_MASTER | I2S_MODE_RX),
    .sample_rate = SAMPLE_RATE,
    .bits_per_sample = I2S_BITS_PER_SAMPLE_16BIT,
    .channel_format = I2S_CHANNEL_FMT_ONLY_LEFT,
    .communication_format = I2S_COMM_FORMAT_STAND_I2S,
    .intr_alloc_flags = 0,
    .dma_buf_count = 8,
    .dma_buf_len = BUFFER_LEN,
    .use_apll = false,
    .tx_desc_auto_clear = false,
    .fixed_mclk = 0
  };
  i2s_driver_install(I2S_PORT, &i2s_config, 0, NULL);
}

/*
* This function sets the pins for the I2S protocol. This includes setting the serial clock (SCK), 
* word select (WS), and serial data (SD).
*/
void i2s_setpin() {
  const i2s_pin_config_t pin_config = {
    .bck_io_num = I2S_SCK,
    .ws_io_num = I2S_WS,
    .data_out_num = -1,
    .data_in_num = I2S_SD
  };
  i2s_set_pin(I2S_PORT, &pin_config);
}

/*
* This is the callable function that initializes the I2S protocol for the digital microphone.
*/
void init_i2s() {
  i2s_install();
  i2s_setpin();
  i2s_start(I2S_PORT);
}

// ------- Write WAV Header -------
/*
* This function writes the WAV header to the buffer. See WAV file documentation for WAV header standard.
*/
void writeWavHeader(uint8_t *buffer, uint32_t audioLen) {
  uint32_t byteRate = SAMPLE_RATE * CHANNELS * BITS_PER_SAMPLE / 8;
  uint32_t totalDataLen = audioLen + 36;

  memcpy(buffer, "RIFF", 4);
  memcpy(buffer + 4, &totalDataLen, 4);
  memcpy(buffer + 8, "WAVEfmt ", 8);

  uint32_t subchunk1Size = 16;
  uint16_t audioFormat = 1; // PCM
  uint16_t blockAlign = CHANNELS * BITS_PER_SAMPLE / 8;

  memcpy(buffer + 16, &subchunk1Size, 4);
  memcpy(buffer + 20, &audioFormat, 2);
  memcpy(buffer + 22, &CHANNELS, 2);
  memcpy(buffer + 24, &SAMPLE_RATE, 4);
  memcpy(buffer + 28, &byteRate, 4);
  memcpy(buffer + 32, &blockAlign, 2);
  memcpy(buffer + 34, &BITS_PER_SAMPLE, 2);
  memcpy(buffer + 36, "data", 4);
  memcpy(buffer + 40, &audioLen, 4);
}

// ------- Initialize Buttons and LED -------
/*
* This function initializes all peripheral components of the hardware. This includes the push button, 
* the RGB light, PSRAM (for buffer store), and the WAV file buffer.
*/
void init_peripherals() {
  // Initialize button and attach button press event to trigger flag
  pinMode(BUTTON_PIN, INPUT_PULLDOWN);
  attachInterrupt(BUTTON_PIN, onButtonPress, RISING);

  // Initialize RGB LED
  pinMode(RED, OUTPUT);
  pinMode(GREEN, OUTPUT);

  // Ensure RGB LED is OFF
  digitalWrite(RED, 0);
  digitalWrite(GREEN, 0);

  // Check for PSRAM initialization
  if (psramFound()) {
    Serial.println("PSRAM is available.");
    Serial.printf("Free PSRAM: %d bytes\n", ESP.getFreePsram());
  } else {
    Serial.println("PSRAM not detected.");
  }

  // Initialize WAV file buffer
  wavBuffer = (uint8_t*) ps_malloc(TOTAL_BYTES);
  if (!wavBuffer) {
    Serial.println("Failed to allocate PSRAM buffer.");
    while (true); // halt program
  }

  // Initialize the last active time
  lastActiveTime = millis();
}

// ------- Initialize WiFi -------
/*
* This function initializes WiFi connection.
*/
void init_WiFi() {
  WiFi.begin(SSID, wifiPW);

  Serial.print("Connecting to Wi-Fi");
  unsigned long starttime = millis();
  while (WiFi.status() != WL_CONNECTED && millis() - starttime < 40 * 1000) {
      Serial.print(".");
      delay(300);
  }

  if (WiFi.status() != WL_CONNECTED) {
    Serial.println("WiFi connection timeout. Restarting device...");
    ESP.restart();
  }

  Serial.println("\nWiFi connected. IP address: ");
  Serial.println(WiFi.localIP());
}

// ------- Timeout Check Function -------
/*
* This function checks how long the device has been inactive and puts the device into deep sleep
* if it has been more than the inactivity time time.
*/
void timeout_check() {
  // Check if the elapsed time since activity is longer than the timeout
  if ((millis() - lastActiveTime >= INACTIVITY_TIMEOUT) && !startRecording) {
    Serial.println("Inactivity timeout reached. Entering deep sleep...");

    // Configure EXT1 wakeup (wake on HIGH from GPIO 2)
    esp_sleep_enable_ext1_wakeup(WAKEUP_MASK, ESP_EXT1_WAKEUP_ANY_HIGH);

    // Properly close WiFi connection
    WiFi.disconnect();

    // Actually go to sleep
    esp_deep_sleep_start();
  }
}

/*
// not needed unless using UCSD WiFi
// This function is an alternative to init_WiFi() that initializes an authenticated WiFi connection (eduroam).
void init_Eduroam() {
  WiFi.mode(WIFI_STA);
  esp_wifi_sta_wpa2_ent_enable();

  esp_wifi_sta_wpa2_ent_set_identity((uint8_t *)EAP_IDENTITY, strlen(EAP_IDENTITY));
  esp_wifi_sta_wpa2_ent_set_username((uint8_t *)EAP_USERNAME, strlen(EAP_USERNAME));
  esp_wifi_sta_wpa2_ent_set_password((uint8_t *)EAP_PASSWORD, strlen(EAP_PASSWORD));

  WiFi.begin(ssid);

  Serial.print("Connecting to eduroam");
  while (WiFi.status() != WL_CONNECTED) {
    delay(1000);
    Serial.print(".");
  }

  Serial.println("\nWiFi connected. IP address: ");
  Serial.println(WiFi.localIP());
}
*/

// ------- Initialize Firebase -------
/*
* This function initializes and authenticates the Firebase Client connection. 
*/
void init_Firebase() {
  Serial.printf("Firebase Client v%s\n\n", FIREBASE_CLIENT_VERSION);
  Serial.println("Initializing app...");

  config.api_key = API_KEY;
  auth.user.email = USER_EMAIL;
  auth.user.password = USER_PW;

  config.token_status_callback = tokenStatusCallback;
  Firebase.reconnectNetwork(true);
  fbdo.setBSSLBufferSize(8192, 2048); // previously 4096, 1024
  Firebase.begin(&config, &auth);
}

// ------- Generate File Name Function
/*
* This function generates a filename for use on the Firebase Storage side. The identifier uses the format {device_id}_{random_num}.
*/
String generate_filename() {
  return "/" + String(DEVICE_ID) + "_" + String(random(100000)) + ".wav";
}

// ------- Audio Helpers -------
/*
* This is a callback function provided from the Firebase library that provides detailed information about errors, upload status, and completion messages.
*/
void fcsUploadCallback(FCS_UploadStatusInfo info)
{
    if (info.status == firebase_fcs_upload_status_init)
    {
        Serial.printf("Uploading file %s (%d) to %s\n", info.localFileName.c_str(), info.fileSize, info.remoteFileName.c_str());
    }
    else if (info.status == firebase_fcs_upload_status_upload)
    {
        Serial.printf("Uploaded %d%s, Elapsed time %d ms\n", (int)info.progress, "%", info.elapsedTime);
    }
    else if (info.status == firebase_fcs_upload_status_complete)
    {
        Serial.println("Upload completed\n");
        FileMetaInfo meta = fbdo.metaData();
        Serial.printf("Name: %s\n", meta.name.c_str());
        Serial.printf("Bucket: %s\n", meta.bucket.c_str());
        Serial.printf("Size: %d\n", meta.size);
        Serial.printf("Download URL: %s\n\n", fbdo.downloadURL().c_str());
    }
    else if (info.status == firebase_fcs_upload_status_error)
    {
        Serial.printf("Upload failed, %s\n", info.errorMsg.c_str());
    }
}

// ------- Record Audio Task
/*
* This is the main function to record and transmit audio from the microphone.
*/
void record_and_transmit() {
  // Check if buffer has been initialized
  if (!wavBuffer) {return;}

  // Write the WAV header to buffer
  writeWavHeader(wavBuffer, AUDIO_BYTES);

  // Turn RGB RED
  digitalWrite(RED, 255);

  // Record audio
  Serial.println("Recording audio...");
  unsigned long starttime = millis(); // get start time
  uint32_t offset = 44;

  // record for specified record time (seconds) or until buffer is full
  while (millis() - starttime < RECORD_TIME * 1000 && offset + BUFFER_LEN * sizeof(int16_t) <= TOTAL_BYTES) {
    size_t bytesRead;
    if(i2s_read(I2S_PORT, sBuffer, sizeof(sBuffer), &bytesRead, portMAX_DELAY) == ESP_OK && bytesRead > 0) {
      memcpy(wavBuffer + offset, sBuffer, bytesRead);
      offset += bytesRead;
    } else {
      Serial.println("I2S read error or buffer overflow.");
      free(wavBuffer);
      return;
    }
  }

  Serial.println("Recording complete. Uploading...");

  // Turn RGB GREEN
  digitalWrite(RED, 0);
  digitalWrite(GREEN, 255);

  // Get filename
  String path = generate_filename();

  // If the Firebase connection fails return
  if (!Firebase.ready()) {return;}

  // If the Firebase upload fails print the error message and return
  if (!Firebase.Storage.upload(
    &fbdo,
    STORAGE_BUCKET,
    wavBuffer,
    offset,
    path,
    "audio/wav",
    fcsUploadCallback)) {

    Serial.println("Firebase Upload Failed: " + fbdo.errorReason());
  }

  // Turn off RGB
  digitalWrite(GREEN, 0);

  return;
}

// ------- Record Audio Task -------
/*
* Main code that runs full audio pipeline. Task is pinned to core and waits for flag to be triggered to begin pipeline.
*/
void main_audio(void *parameter) {
  while (true) {
    // Wait for button press
    if (startRecording) {
      // Reset inactivity time to ensure deep sleep doesn't happen mid recording
      lastActiveTime = millis();

      // Record and transmit task
      record_and_transmit();

      // Reset inactivity time to after recording and upload finish
      lastActiveTime = millis();

      // Turn off recording flag
      startRecording = false;
    }

    // Add a delay
    vTaskDelay(100 / portTICK_PERIOD_MS);
  }
}
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

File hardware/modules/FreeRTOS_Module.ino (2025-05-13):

#include <driver/i2s.h>
#include <SD.h>
#include <SPI.h>

// --- Pin Definitions ---
#define I2S_WS 6
#define I2S_SD 5
#define I2S_SCK 4
#define BUTTON_PIN 21
#define INTERNAL_LED 48
#define SD_CS 10

// --- I2S and Recording Settings ---
#define I2S_PORT I2S_NUM_0
const uint32_t SAMPLE_RATE = 44100;
const uint16_t BITS_PER_SAMPLE = 16;
const uint16_t CHANNELS = 1;
#define BUFFER_LEN 512  
#define RECORD_TIME 30

int16_t sBuffer[BUFFER_LEN];
volatile bool startRecording = false;

// --- ISR for Button Press ---
void IRAM_ATTR onButtonPress() {
  startRecording = true;
}

// --- I2S Setup ---
void i2s_install() {
  const i2s_config_t i2s_config = {
    .mode = (i2s_mode_t)(I2S_MODE_MASTER | I2S_MODE_RX),
    .sample_rate = SAMPLE_RATE,
    .bits_per_sample = I2S_BITS_PER_SAMPLE_16BIT,
    .channel_format = I2S_CHANNEL_FMT_ONLY_LEFT,
    .communication_format = I2S_COMM_FORMAT_STAND_I2S,
    .intr_alloc_flags = 0,
    .dma_buf_count = 8,
    .dma_buf_len = BUFFER_LEN,
    .use_apll = false,
    .tx_desc_auto_clear = false,
    .fixed_mclk = 0
  };
  i2s_driver_install(I2S_PORT, &i2s_config, 0, NULL);
}

void i2s_setpin() {
  const i2s_pin_config_t pin_config = {
    .bck_io_num = I2S_SCK,
    .ws_io_num = I2S_WS,
    .data_out_num = -1,
    .data_in_num = I2S_SD
  };
  i2s_set_pin(I2S_PORT, &pin_config);
}

// --- Write WAV Header ---
void writeWavHeader(File &file, uint32_t totalAudioLen) {
  uint32_t byteRate = SAMPLE_RATE * CHANNELS * BITS_PER_SAMPLE / 8;
  uint32_t totalDataLen = totalAudioLen + 36;

  byte header[44];

  memcpy(header, "RIFF", 4);
  memcpy(header + 4, &totalDataLen, 4);
  memcpy(header + 8, "WAVE", 4);
  memcpy(header + 12, "fmt ", 4);

  uint32_t subchunk1Size = 16;
  uint16_t audioFormat = 1; // PCM
  memcpy(header + 16, &subchunk1Size, 4);
  memcpy(header + 20, &audioFormat, 2);
  memcpy(header + 22, &CHANNELS, 2);
  memcpy(header + 24, &SAMPLE_RATE, 4);
  memcpy(header + 28, &byteRate, 4);
  uint16_t blockAlign = CHANNELS * BITS_PER_SAMPLE / 8;
  memcpy(header + 32, &blockAlign, 2);
  memcpy(header + 34, &BITS_PER_SAMPLE, 2);
  memcpy(header + 36, "data", 4);
  memcpy(header + 40, &totalAudioLen, 4);

  file.write(header, 44);
}
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

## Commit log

2025-04-19 add pytest.yml, sample tests
2025-04-30 Create hardware.ino
    Add onboard for device hardware
2025-05-08 Update hardware.ino
    Updated functionality so that the LED functions when button is pressed. Also, updated initialization of peripherals (buttons, LED, etc)
2025-05-12 added user object, updated create account for actual new user flow
2025-05-12 connecting create account flows, minor chnages to .gitingore etc
2025-05-12 auth code updated for user with device, created Info.plist manually
2025-05-12 user registration updated to support users with and without devices
2025-05-12 user registration updates to support users with and without device
2025-05-12 completed login flow, adding device selection code e2e.
2025-05-12 Organized login flow into folders
2025-05-13 Built the learn more flow
2025-05-17 Update hardware.ino
    Update to define new pin schema and LED (no RGB) for XIAO ESP32-S3 board
2025-05-17 Update README.md
    Updated board being used
2025-05-17 New modules for temperature and deep sleep
    - Test module to monitor internal temperature of chip
    - Test module to implement deep sleep when device is not in use
2025-05-17 Update hardware.ino
    - Removed ESP32-S3-DevKitC-1-N16R8 related code
    - Added deep sleep timeout (5 min inactivity timeout)
    - Removed line # comments due to maintenance overhead
2025-06-02 Update README.md
    Added info about 3D printing the casing
2025-06-02 Update README.md
    Added information for the physical hardware assembly
2025-06-02 Add design files and BOM
    Added design files and BOM
    [Battery Holder.3mf, Casing Cover.3mf, ESP32 Mounting Plate.3mf, Mic and Diaphragm Mount.3mf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]
2025-06-02 Create assembly.md
    Added instructions to assemble hardware
2025-06-02 Moved files
    [Battery Holder.3mf, Casing Cover.3mf, ESP32 Mounting Plate.3mf, Mic and Diaphragm Mount.3mf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]
2025-06-03 Update Button_Mic_Module.ino
    Switched module to work with RGB diode rather than built in LED on original ESP32-S3 (not XIAO)
2025-06-03 Update Button_Module.ino
    Updated pin for button (GPIO 2 on XIAO ESP32-S3)
2025-06-03 Update XIAO_Button_Mic_Module.ino
    Fixed button pin
2025-06-03 Update hardware.ino
    Added functionality that would reset ESP32 if WiFi takes too long to connect
